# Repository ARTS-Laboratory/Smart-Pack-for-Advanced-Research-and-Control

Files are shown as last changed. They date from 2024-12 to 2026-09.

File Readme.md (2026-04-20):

# Smart-Pack-for-Advanced-Research-and-Control (SPARC)
The SPARC Pack is an open-source, research-grade battery system designed to advance thermal and electro-thermal modeling techniques while integrating state-of-the-art sensing and Battery Management System (BMS) technologies. Its modular design supports both cylindrical and pouch cell configurations, enabling cutting-edge investigations into battery performance, health, and reliability under diverse operating conditions.

## Variations

### Camden
A pack designed around the Samsung 30Q as a 10S1P nominal 40 V pack. 

## Licensing and Citation

This work is licensed under a Creative Commons Attribution-ShareAlike 4.0 International License [cc-by-sa 4.0].



Cite this as: 

@Misc{ARTSLabSmartPackAdvanced,    
  author = {ARTS-Lab},  
  howpublished = {GitHub},  
  title  = {Smart-Pack-for-Advanced-Research-and-Control},    
  groups = {ARTS-Lab},    
  url    = {https://github.com/ARTS-Laboratory/Smart-Pack-for-Advanced-Research-and-Control},   
  note  = {Accessed: Month dd, yyyy},   
}

<p align="center">
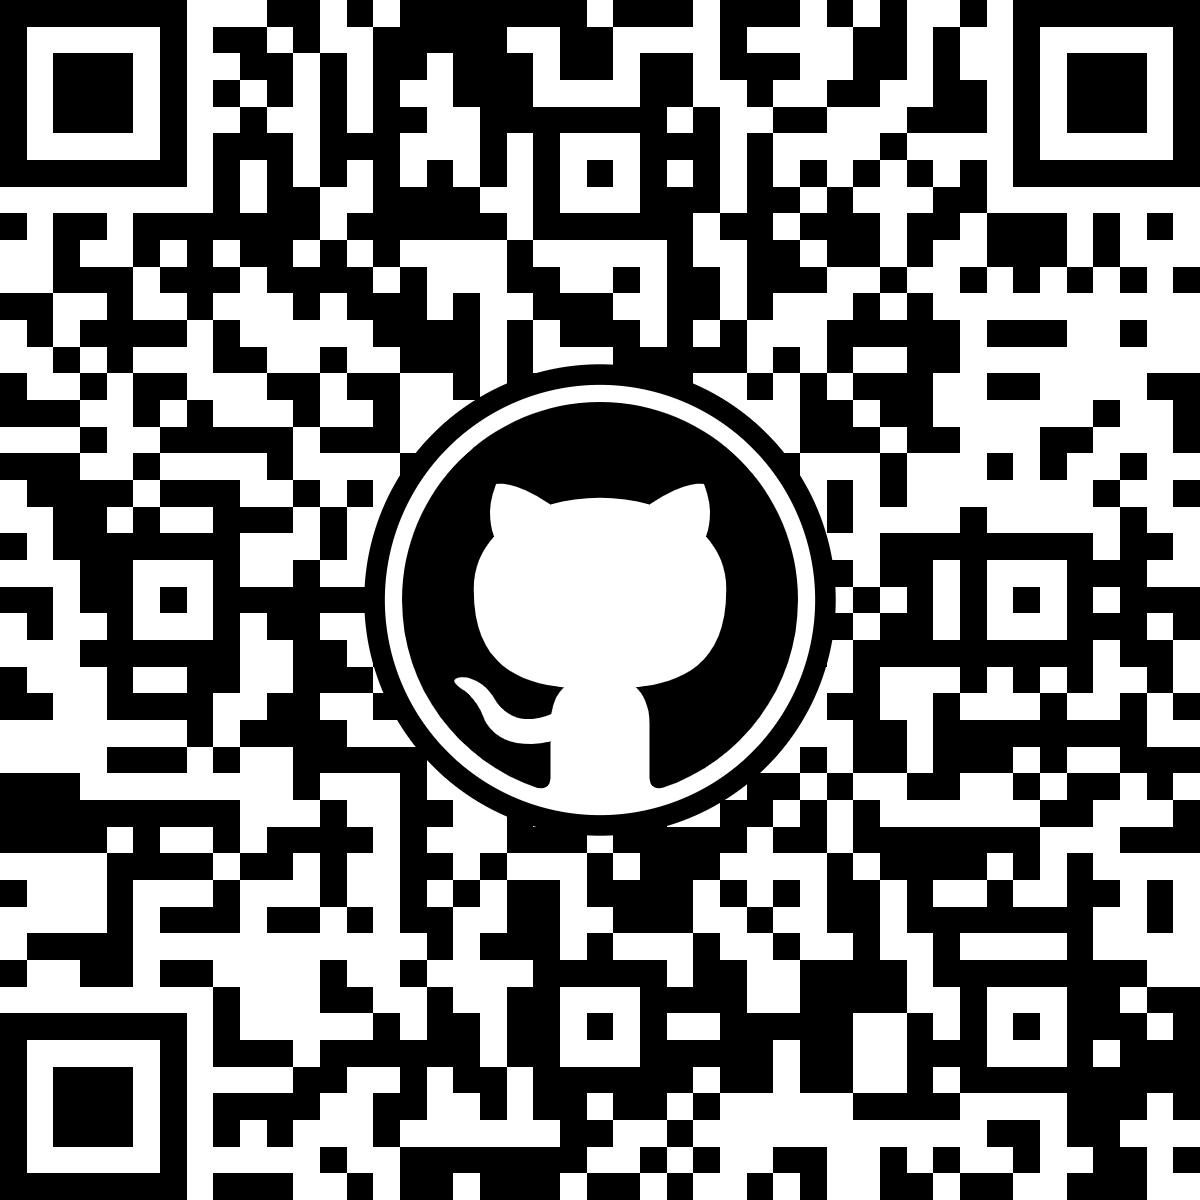
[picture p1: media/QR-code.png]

</p>
<p align="center">
QR code for repo.
</p>

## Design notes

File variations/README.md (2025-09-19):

# Variations
Variations of the battery packs are named after cities in South Carolina with Amtrack Stations.

## Camden
A pack designed around the Samsung 30Q as a 10S1P nominal 42 V 30 Ah pack. 

## Columbia
A pack designed around the Samsung 40T as a 10S1P nominal 42 V 40 Ah pack. 

## Florence
A pack designed around the Hakadi 18650E-1500 as a 10S1P nominal 30 V 15 Ah pack. 

## Denmark
A pack designed around the LithiumWerks APR18650m1B as a 10S1P nominal 33 V 11.5 Ahr pack.

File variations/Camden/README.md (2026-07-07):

# Camden
A pack designed around the Samsung 30Q as a 10S1P nominal 42 V 30 Ah pack. 

## V0.1.0 
1. Inital desings for 10S1P
1. Uses a 3-4-3 layout

## V0.2.0
1. stable 3D print setups

## V0.2.1
1. Sense wires on the packs.
1. Snap fits.
1. Single design for top and bottom.

## V0.2.2
1. More defined DIN-rail system
2. Different plastic frames form top and bottom
3. PCBs for BMS

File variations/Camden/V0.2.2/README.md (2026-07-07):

# Camden V0.2.2
This version puts the pack onto a back board with a DIN Rail

This project uses KiCAD 9.0.5 https://downloads.kicad.org/kicad/windows/explore/stable/download/kicad-9.0.5-x86_64.exe and Inventor 2025 Q2

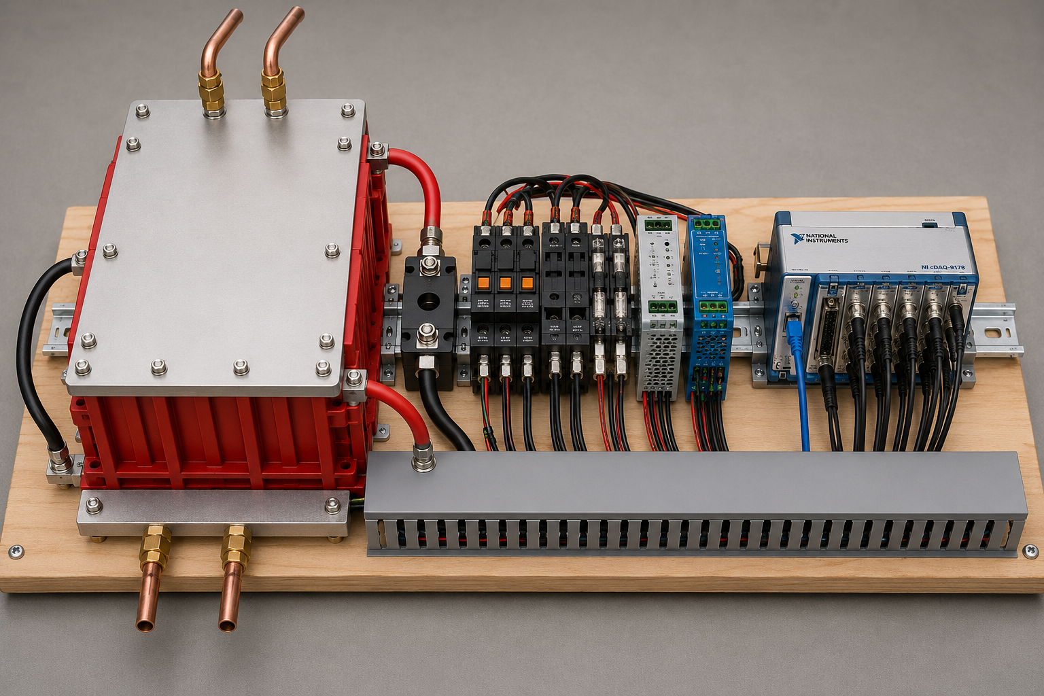
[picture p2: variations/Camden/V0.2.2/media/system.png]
 <br> 
<p style="text-align: center;"> Desing vison image of the proposed SPARC system.</p>

</p>

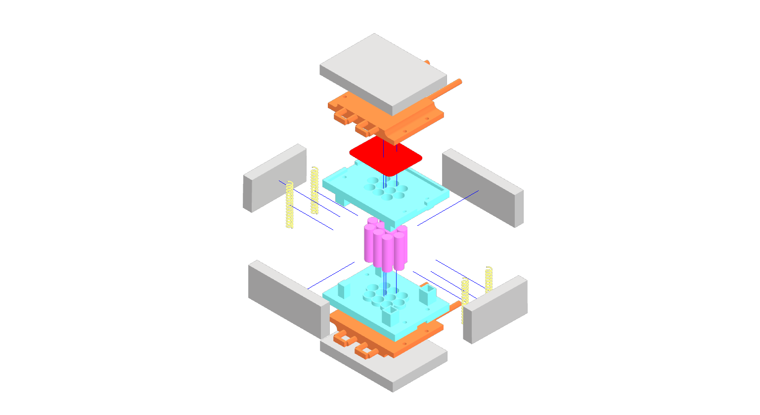
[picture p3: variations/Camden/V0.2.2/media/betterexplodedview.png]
 <br> 
<p style="text-align: center;"> The battery pack design.</p>

</p>

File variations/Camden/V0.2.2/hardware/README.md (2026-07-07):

# Hardware

## Todo notes (mark when done)
1. Make a top and bottom
1. Delete all the CAD files that are nto 18550 and you don't need. 
1. Extend the gap between the slot down and the first and last cell. Move the edge out more if needed. 
1. Rotate bolt hole 90* so the flat end faces out. 
1. Label them cells 0-9 
1. Replace ARTS-LAB with "Frame top" or whatever the name of the inventor file is. 
1. Add ARTS-LAB but bigger and on the side as just Branding. 
1. Think on the connectors, the will be updates, but maybe not now.

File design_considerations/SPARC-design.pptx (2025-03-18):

## Smart-Pack-for-Advanced-Research-and-Control (SPARC)

## Why Develop a Modular, Sensor-Rich Battery System?

- Supports Next-Generation Energy Storage
  - Enables research on distributed energy systems and high-performance battery management
  - Facilitates scalability for a wide range of power applications
- Enhances Digital Twin Development
  - Real-time, high-fidelity data streams enable dynamic model validation and predictive analytics
  - Integrated sensors allow continuous updates to electrochemical, thermal, and mechanical models
- Enables Flexible and Configurable Testing
  - Modular 42V (10S1P) design allows for series/parallel stacking to replicate different battery pack architectures
  - Supports multiple cell sizes and chemistries (e.g., 18650, 21700, NMC, LFP) for diverse application studiesImproves
- Advanced Battery Control and Monitoring
  - High-resolution BMS with CompactDAQ integration enables real-time state estimation and anomaly detection
  - Adaptive energy management through advanced control strategies

## Why Not Just Buy a Battery Pack?

- It’s Not That Simple
  - Off-the-shelf battery packs are designed for consumer or industrial use, not for research and experimentation
  - Most commercial packs come with proprietary BMS systems that restrict access to raw data, limiting the ability to monitor and analyze cell-level behavior
- Limited Experimental Flexibility
  - Research often requires testing individual cells and full packs under identical conditions, which isn’t possible with third-party pack builders
  - By sourcing cells from a single batch, researchers can compare degradation, thermal response, and electrochemical performance at both cell and pack levels
  - Pack design constraints in commercial solutions prevent studies on alternative cooling strategies, advanced sensing, and new control architectures
- Need for Custom Sensing and Instrumentation
  - Commercial battery packs do not support high-resolution instrumentation, such as differential voltage sensing, strain monitoring, and acoustic emissions
  - In research, advanced sensing capabilities are critical for developing and validating digital twins, studying failure mechanisms, and improving predictive modeling
  - Custom-built packs allow for direct integration with external control and data acquisition systems, ensuring researchers have full control over charging, discharging, and monitoring parameters

## What Will the Battery Module look like?


Thermal pad

Cold plate

Assembly springs

Cells

Insulation

Cell holder

## What Will the BMS Look Like?

BMS Control Board

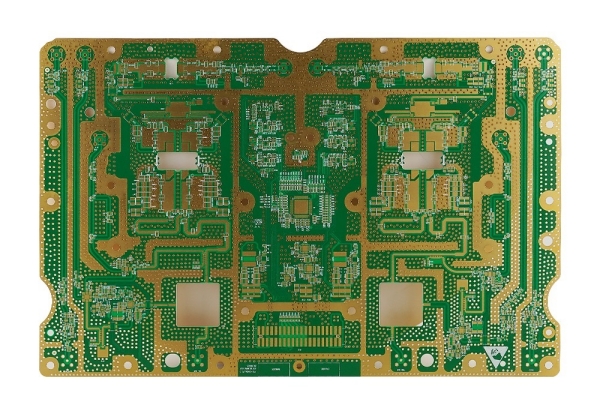
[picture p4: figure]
Custom PCB-The Ultimate Guide-ucreatepcb.com
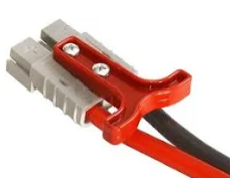
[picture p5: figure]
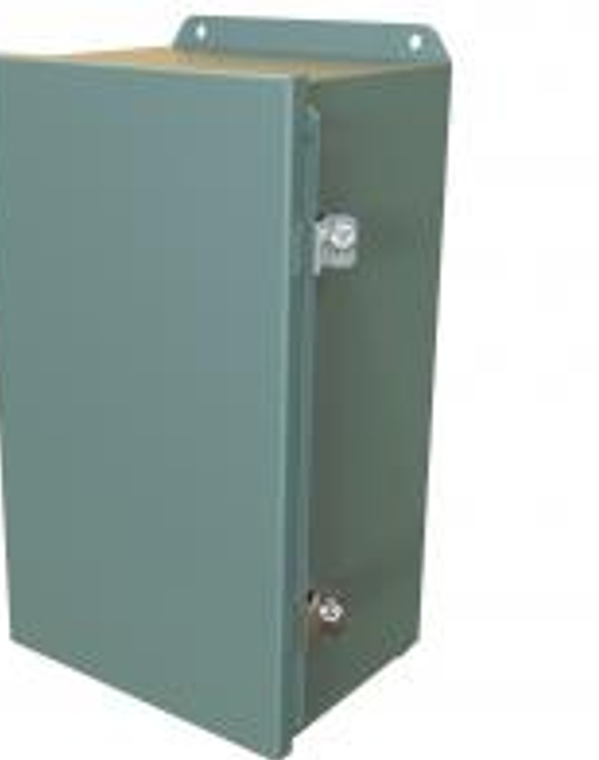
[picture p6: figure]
N4,12 J Box Hinged - 14x8x6 - Steel/Gray

Battery

Cost:
- $20,000 fully-instrumented
- $10,000 typical deployment
- $4,000 minimal viable

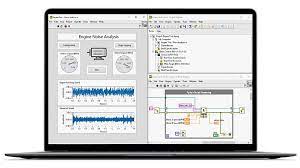
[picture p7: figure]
Zustandsüberwachung für die industrielle Fertigung - NI
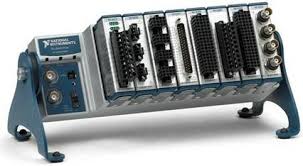
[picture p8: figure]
CompactDAQ - Wikipedia

cDAQ based DAQ

## What Features will the Pack Have

Comprehensive Sensing Capabilities
- Voltage Monitoring – Individual cell voltages and differential voltage across each cell for precise state-of-charge (SOC) estimation
- Temperature Sensors – Each cell will have dedicated temperature monitoring, ensuring thermal stability and safety
- Current Sensors – High-resolution current measurement for charge/discharge tracking and efficiency analysis
- Strain Gauges – Integrated strain sensing on cells and pack components to monitor mechanical deformation and aging effects
- Acoustic Emission Sensors – Captures high-frequency signals from crack formation, gas evolution, and early failure indicators

Advanced Battery Management Features
- Cell-Level Monitoring – Every cell is individually monitored for voltage, temperature, and strain, allowing detailed analysis of cell-to-cell variations
- Cell Balancing – Passive balancing to start, ensuring even charge distribution and extending pack lifetime
- Customizable Data Sampling – Fully open data acquisition interface, allowing researchers to modify sampling rates and data logging parameters
Open-Access and Reconfigurable Design
- Fully Open Front Panel – Allows for easy access to all monitoring points, enabling rapid sensor modifications, data acquisition customization, and external integrations
- Flexible Control Integration – Can directly support adaptive BMS algorithms and digital twin updates

## Thank You for Your Time

- Name: Austin Downey
- Title: Associate Professor
- Email: austindowney@sc.edu
- Lab GitHub: github.com/arts-laboratory

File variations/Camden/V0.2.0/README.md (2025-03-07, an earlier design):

# Camden V0.2

 <br> 
The battery pack design. 
</p>

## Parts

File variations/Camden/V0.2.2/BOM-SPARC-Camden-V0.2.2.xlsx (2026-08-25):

Designator | Component | MFR Part Number | Amount | Individual Cost | Total Cost | Notes | Vendor 1 | Vendor 2 | Vendor 3 | Vendor 4 | Vendor 5 | Vendor 6
Cells | Samsung 30Q |  | 10 | $8.22 | $82.20 |  | https://www.batteryjunction.com/products/samsung-30q-18650-3000-flat
power plug | Powerwerx PanelPlateSB1 for Anderson SB50 Series Connectors |  | 1 | $9.99 | $9.99 |  | https://powerwerx.com/anderson-sb50-panel-chassis-mount
Box | RITTAL Enclosure: Steel, 15 in x 13 in x 10 in, NEMA 4, Solid Cover, Hinged |  | 1 | $234.98 | $234.98 |  | https://www.grainger.com/product/RITTAL-Enclosure-Steel-5AAC4?opr=ILOF
Controller | cRIO-9054 |  | 1 | $3427.00 | $3427.00 |  | https://www.ni.com/en-us/shop/model/crio-9054.html | https://www.digikey.com/en/products/detail/ni/786425-01/16648375?s=N4IgTCBcDaIMYCUCSB5AtATgAwFYAsIAugL5A
strain DAQ | NI-9236 |  | 1 | $3048.00 | $3048.00 |  | https://www.ni.com/en-us/shop/model/ni-9236.html | https://www.digikey.com/en/products/detail/ni/785996-01/15219166
~~voltage module~~ | ~~NI-9221~~ |  | ~~2~~ | ~~$1106.00~~ | ~~$2212.00~~ |  | ~~https://www.ni.com/en-us/shop/model/ni-9221.html | ~~https://www.digikey.com/en/products/detail/ni/779373-01/15219106~~
Foam board | R-10 XPS Rigid Foam Board |  | 1 | $56.97 | $56.97 |  | https://www.homedepot.com/p/Owens-Corning-FOAMULAR-NGX-F-250-2-in-x-4-ft-x-8-ft-SSE-R-10-XPS-Rigid-Foam-Board-Insulation-52DDNGX/315197962
22 gauge black wire | APPROVED VENDOR Automotive Wire: TXL, 100 ft, 1 Conductor, 22 AWG, Black, 60 V Volt |  | 1 | $10.72 | $10.72 |  | https://www.grainger.com/product/Automotive-Wire-TXL-862FY9
22 gauge red wire | APPROVED VENDOR Automotive Wire: TXL, 100 ft, 1 Conductor, 22 AWG, Red, 60 V Volt |  |  | $10.72 | $10.72 |  | https://www.grainger.com/product/Automotive-Wire-TXL-862FZ5
6 gauge red and black wire | Wire-RB-06-25 |  | 1 | $90.99 | $90.99 |  | https://powerwerx.com/red-black-bonded-zip-cord
strain gauge (9 ft lead) | C4A-06-235SLA-350-39P |  | 1 | $162.72 | $162.72 |  | https://shop.micro-measurements.com/my_cart_item_list.php?v_cat_code=STRESS_ANALYSIS_STRAIN_GAGE | https://www.digikey.com/en/products/detail/micro-measurements-division-of-vishay-precision-group/MMF404146/9857834
strain gauge (3 ft lead) | C4A-06-235SLA-350-33P |  | 1 | $162.72 | $162.72 |  | https://shop.micro-measurements.com/my_cart_item_list.php?v_cat_code=STRESS_ANALYSIS_STRAIN_GAGE | https://www.digikey.com/en/products/detail/micro-measurements-division-of-vishay-precision-group/C4A-06-235SLA-350-33P/16580673
thermocouple probe | TEMPCO Thermocouple Probe: Thermocouple, Type K, 3/16 in x 3 in Probe, Grounded, Split Leads |  | 2 | $23.08 | $46.16 |  | https://www.grainger.com/product/TEMPCO-Thermocouple-Probe-Thermocouple-3AAA2?opr=ODOH&analytics=FM:Order%20History
thermocouple fitting | TEMPCO Compression Fitting: 1/8 in MNPT, For Sensor with 3/16 in OD Sheath Sensor Type |  | 2 | $7.26 | $14.52 |  | https://www.grainger.com/product/TEMPCO-Compression-Fitting-1-8-in-5ZY28?opr=ODOH&analytics=FM:Order%20History
Strain Gauge Glue (cheap option) | LOCTITE Instant Adhesive: 401, Plastics, 0.1 fl oz, Tube |  | 1 | $8.98 | $8.98 | This is the low-cost option, and we should not really use it. | https://www.grainger.com/product/LOCTITE-Instant-Adhesive-401-2VFG1?opr=ODOH&analytics=FM:Order%20History
Strain Gauge Glue | LOCTITE Instant Adhesive: 401, Plastics, 0.1 fl oz, Tube |  | 1 | $8.98 | $8.98 |  | https://www.grainger.com/product/LOCTITE-Instant-Adhesive-401-2VFG1?opr=ODOH&analytics=FM:Order%20History
cold plate | Ohmite CP4A-114A-108E-ND |  | 2 | $74.89 | $149.78 |  | https://www.digikey.com/en/products/detail/ohmite/CP4A-114A-108E/3439805
thermal pad | t-Global Technology 1168-TG-AH486-150-150-1.0-0-ND |  | 2 | $10.17 | $20.34 |  | https://www.digikey.com/en/products/detail/t-global-technology/TG-AH486-150-150-1-0-0/3042048
Barb fitting | SPEEDAIRE Barbed Hose Fitting: For 5/16 in Hose I.D., Hose Barb x NPT, 5/16 in x 1/4 in Fitting Size |  | 8 | $1.77 | $14.16 |  | https://www.grainger.com/product/SPEEDAIRE-Barbed-Hose-Fitting-For-3-6AFN8
panel mount dual female mpt | Anchor Coupling: Brass, 3/8 in x 3/8 in Fitting Pipe Size, Male NPT x Female NPT |  | 2 | $23.66 | $47.32 |  | https://www.grainger.com/product/PARKER-Anchor-Coupling-Brass-13Y869?opr=ODOH&analytics=FM:Order%20History
braded PVC tubing | Tubing: PVC, 3/8 in Inside Dia, 1/2 in Outside Dia, 5 ft Lg, Clear, Polyester Braid |  | 1 | $15.02 | $15.02 |  | https://www.grainger.com/product/Tubing-PVC-742T39?gclsrc=aw.ds&gad_source=1&gad_campaignid=21369463827
hose clamp | Fuel Injection Hose Clamp: Zinc-Plated Steel Band, 1/2 in – 9/16 in Dia., SAE # 6, 10 PK |  | 1 | $12.46 | $12.46 |  | https://www.grainger.com/product/Fuel-Injection-Hose-Clamp-5CZC5
panel Ethernet | FINECABLES Connector: Cat5e/Cat6, Industrial, Panel, Female, Phosphor Bronze, IP67, Female |  | 1 | $15.13 | $15.13 |  | https://www.grainger.com/product/808CD1?gad_source=1&gad_campaignid=21375776111&gclsrc=aw.ds
DIN rail power supply | MEAN WELL USA Inc. 1866-3518-ND |  | 1 | $29.30 | $29.30 |  | https://www.digikey.com/en/products/detail/mean-well-usa-inc/NDR-120-24/7705220
DIN Rail | APPROVED VENDOR Mounting Track: DIN Rail Mounting, Aluminum, 35 mm Wd, 305 mm Lg |  | 1 | $4.09 | $4.09 |  | https://www.grainger.com/product/Mounting-Track-DIN-Rail-Mounting-18Z759
DIN Rail 80 amp breaker | SIEMENS IEC Supplementary Protector: 80 A Amps, 72V DC, 10kA at 230/400V AC, Screw Clamp |  | 1 | $147.52 | $147.52 |  | https://www.grainger.com/product/SIEMENS-IEC-Supplementary-Protector-30XZ33
power contacts | Anderson Power Products 5900-BK |  | 4 | $1.45 | $5.80 |  | https://www.digikey.com/en/products/detail/anderson-power-products-inc/5900-BK/10650563
Ethernet cable | MONOPRICE Voice and Data Patch Cord: Unshielded, Cat 5e, 1 ft |  | 1 | $1.46 | $1.46 |  | https://www.grainger.com/product/5PZR3?gclsrc=aw.ds&gad_source=1&gad_campaignid=21379885351
thermocouple input module | NI-9213 |  | 1 | $2195.00 | $2195.00 |  | https://www.ni.com/en-us/shop/model/ni-9213.html | https://www.digikey.com/en/products/detail/ni/785185-01/15218920
TEMPCO Thermocouple Wire | TEMPCO Thermocouple Wire: Type J, 20 AWG Conductor Size, 100 ft |  | 1 | $99.89 | $99.89 |  | https://www.grainger.com/product/TEMPCO-Thermocouple-Wire-Type-K-3AGF3
Thermocouple, Type K | Bead Wire Temperature Probe: Thermocouple, Type K, Ungrounded, Mini Plug, Bolt-On |  | 10 | $6.92 | $69.20 |  | https://www.grainger.com/product/Bead-Wire-Temperature-Probe-4JPL6
D-sub 25 break out | Phoenix Contact 2761619 |  | 2 | $72.75 | $145.50 |  | https://www.digikey.com/en/products/detail/phoenix-contact/2761619/349453
voltage sense wire | 22 gauge solid hook up wire |  | 5 | $3.44 | $17.20 |  | https://www.digikey.com/en/products/detail/sparkfun-electronics/08023/6833929
6 gauge ring connectors | Molex 0191930226 |  | 2 | $1.15 | $2.30 |  | https://www.digikey.com/en/products/detail/molex/0191930226/1952713
Nickel Strips | Nickel Strips For Lithium Battery Pack Welding (10m 0.2X6mm) |  | 1 | $14.65 | $14.65 |  | https://www.aliexpress.us/item/3256805148780496.html?gatewayAdapt=glo2usa4itemAdapt
3/8 in Tee | Tee: Red Brass, 3/8 in x 3/8 in x 3/8 in Fitting Pipe Size, Female NPT x Female NPT x Female NPT |  | 2 | 9.85 | $19.70 |  | https://www.grainger.com/product/Tee-Red-Brass-1VEZ1?opr=PDPRRDSP&analytics=dsrrItems_1CPF5
PLA | PLA Basic - red |  | 1 | $19.99 | $19.99 |  | https://us.store.bambulab.com/products/pla-basic-filament?id=40475107000456
115V power plug | IEC C14 SCREW ON PANEL MOUNT W |  | 1 | $1.87 | $1.87 |  | https://www.digikey.com/en/products/detail/io-audio-technologies/IO-C14SP-63/21379594?gad_source=1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
Strain Gauge Coating | CONFORMAL COATING UL 94V-0 |  | 1 | $22.56 | $22.56 |  | https://www.digikey.com/en/products/detail/mg-chemicals/419D-55ML/9657990
tee to thermocouple reducer | Hex Bushing: Brass, 3/8 in x 1/8 in Fitting Pipe Size, Male NPT x Female NPT, Class 150 |  | 2 | 2.1 | $4.20 |  | https://www.grainger.com/product/Hex-Bushing-Brass-6AYW6
pipe through washerers | Flat Washer: 18-8, Stainless Steel, 1 in Screw Sz, 1.063 in In Dia, 2 in Out Dia, 18-8, 5 PK |  | 4 | $3.75 | $15.00 |  | https://www.grainger.com/product/Flat-Washer-18-8-22UG44
Pump | Kamoer DIP1500 Peristaltic Pump 24V 1500Ml/Min High Flow Intelligent |  | 1 | 299.54 | $299.54 |  | https://www.ebay.com/itm/405898925209?_skw=Kamoer+DIP+1500+Peristaltic+Pumps&itmmeta=01K6KVSWHYJSNG6EA2PQ3BRXEZ
stright 3/8 compression fitting | APPROVED VENDOR Compression Fitting Adapter: 3/8 in OD x 3/8 in Pipe Fitting Size, Brass |  | 2 | 6.74 | $13.48 | If you have 1 of these, you could get rid of one of the 3/8 barb fittings from the tee to the pipe | https://www.grainger.com/product/Compression-Fitting-Adapter-46M551
1 inch Hole Saw | MILWAUKEE Hole Saw: 1 in Saw Dia., 3.5 Teeth per Inch, 1 5/8 in Max. Cutting Dp, Bi-Metal |  | 1 | 15.89 | $15.89 |  | https://www.grainger.com/product/MILWAUKEE-Hole-Saw-1-in-Saw-Dia-856EV8 (https://nam02.safelinks.protection.outlook.com/?reserved=0)
Extension Spring | Music-Wire Steel Extension Springs with Hook Ends |  | 4 | $2.07 | $8.28 | the total cost is actually the price of 6 since that is the lowest it is sold at | https://www.mcmaster.com/9432K48/ | https://www.fastenal.com/product/details/923785687
contact bolt | Hex Head Cap Screw: Stainless Steel, A2, Plain, M6-1.00, Coarse, 16 mm lg, |  | 1 | $4.36 | $4.36 | pack of 50, need 2 | https://www.grainger.com/product/Hex-Head-Cap-Screw-Stainless-22TF95
contact nut | Hex Nut: Std Hex, M6x1.00 Thread, 10 mm Hex Wd, 5 mm Hex Ht, Stainless Steel, 18-8, Plain, 50 PK |  | 1 | $2.73 | $2.73 | pack of 50, need 2 | https://www.grainger.com/product/Hex-Nut-Std-Hex-22YK33
contact washer | Flat Washer: 18-8, Stainless Steel, M6 Screw Sz, 6.62 mm In Dia, 12 mm Out Dia, 18-8, 50 PK |  | 1 | $1.20 | $1.20 | pack of 50, need 2 | https://www.grainger.com/product/Flat-Washer-18-8-26WC34
NI Analog Voltage in | NI-9209 with D-sub (783729-01) |  | 1 | $1414.12 | $1414.12 |  | https://www.ni.com/en/shop/hardware/voltage/model-ni-9209 | https://www.digikey.com/en/products/detail/ni/783729-01/15219085 | https://www.newark.com/ni/783729-01/ni-9209-voltage-input-module-24bit/dp/13AJ4083
Dsub connector | Amphenol ICC (FCI) D37S13A6GX00LF |  | 1 | $7.37 | $7.37 |  | https://www.digikey.com/en/products/detail/amphenol-cs-fci/D37S13A6GX00LF/1538196
Dsub cable | CABLE DB37M/F DBL SHLD 1' |  | 1 | $108.06 | $108.06 |  | https://www.digikey.com/en/products/detail/l-com/CS2N37MF-1/21287760
wire duct | Thomas & Betts Wiring Duct, 2 × 2 in, 72 in, PVC, Gray | TYD2X2WPG6 | 1 | $34.10 | $34.10 | Wide-slot, screw-mount | https://www.grainger.com/product/THOMAS-BETTS-Wiring-Duct-2-in-Nom-Wd-53UH84
wire duct cover | Thomas & Betts Wiring Duct Cover, 2 in, 72 in, PVC, Gray | TYD2CPG6 | 1 | $13.76 | $13.76 | Snap-on cover for 2 in wiring duct | https://www.grainger.com/product/THOMAS-BETTS-Wiring-Duct-Cover-PVC-53UH87
 |  |  |  | Total | $14517.78

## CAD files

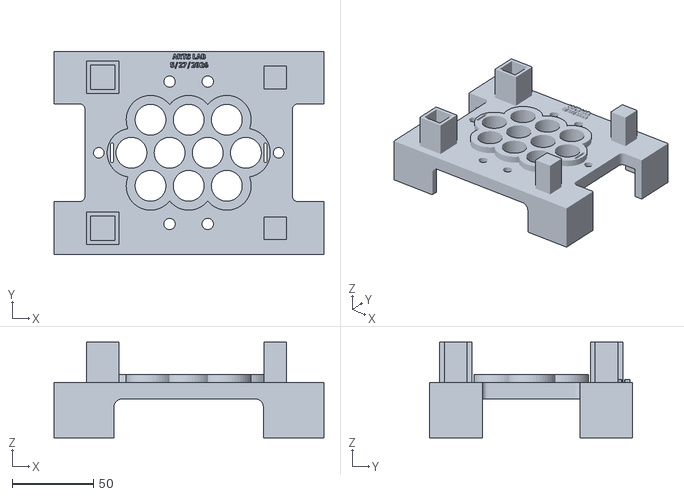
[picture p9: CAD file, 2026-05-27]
variations/Camden/V0.2.2/hardware/18650_Pack_CAD/Pillars_Cellcase_18650.stl
166.3 x 125.1 x 59.0

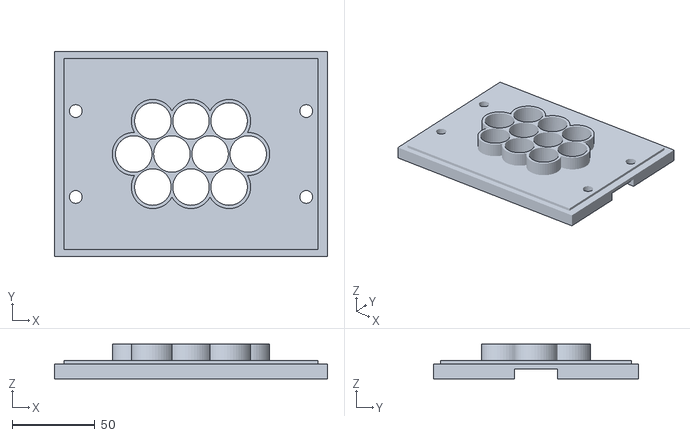
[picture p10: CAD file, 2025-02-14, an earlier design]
variations/Camden/V0.1.0/CELLCASE21700.stl
164.6 x 123.7 x 21.0

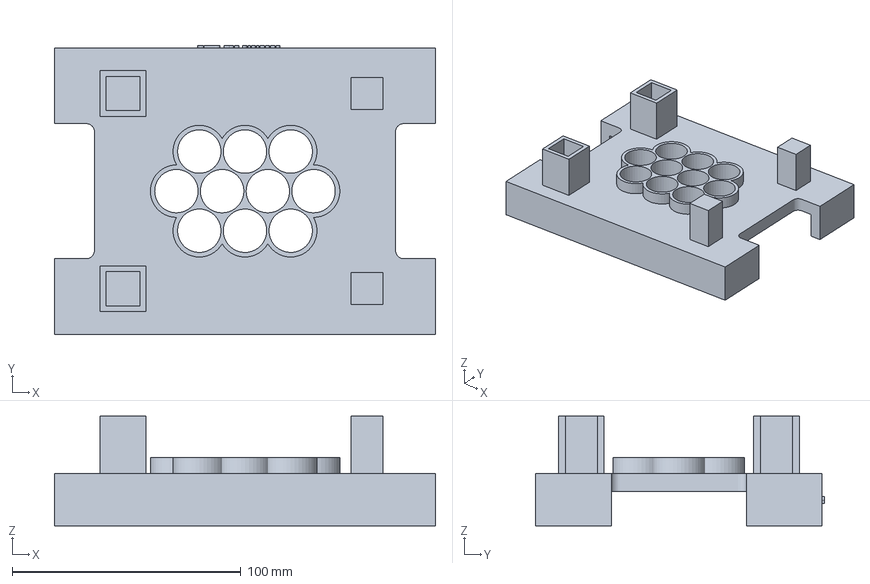
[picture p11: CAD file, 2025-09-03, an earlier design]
variations/Camden/V0.2.0/PILLARSCELLCASE18650.3mf
166.7 x 126.4 x 48.0 mm

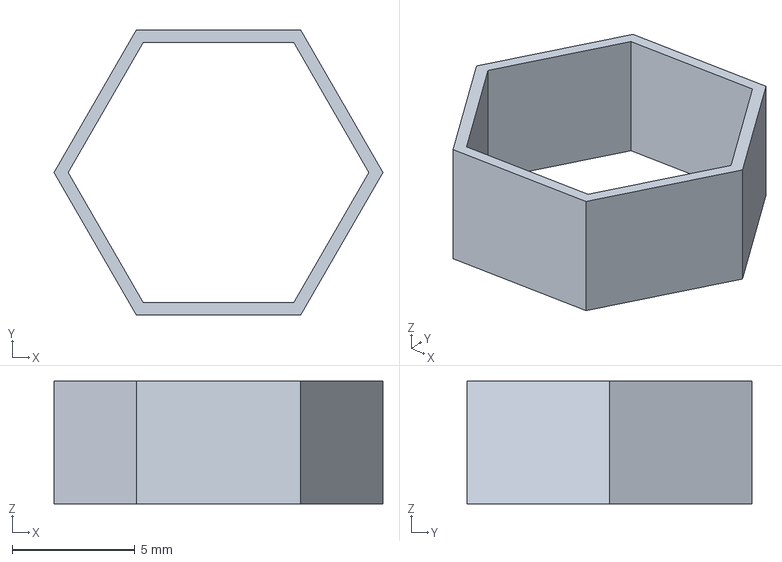
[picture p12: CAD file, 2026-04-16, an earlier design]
variations/Camden/V0.2.1/hardware/18650_Pack_Cad/tolerance_test.3mf
13.4 x 11.6 x 5.00 mm

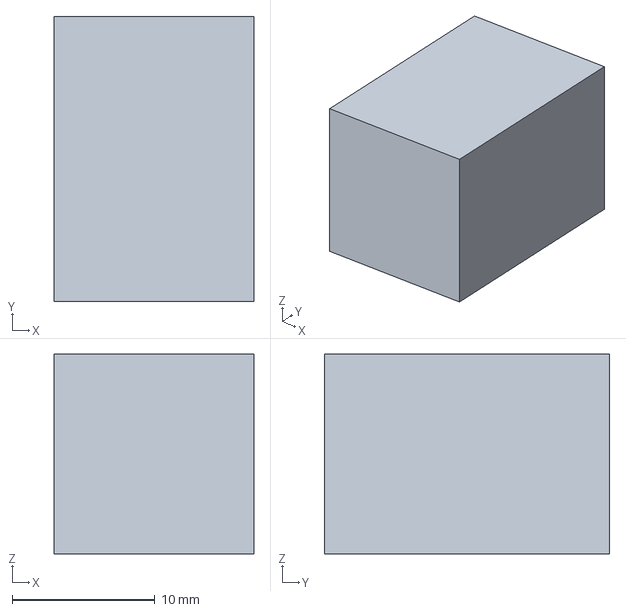
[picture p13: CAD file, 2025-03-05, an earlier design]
variations/Camden/V0.2.1/hardware/Old_Versions/PILLARStest.3mf
14.0 x 20.0 x 14.0 mm

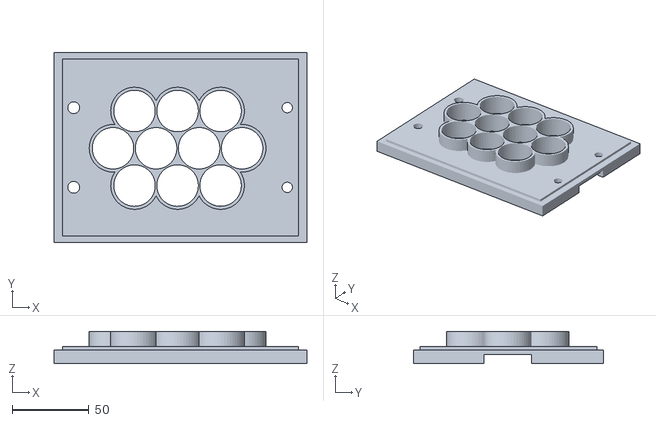
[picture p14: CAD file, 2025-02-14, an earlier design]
variations/Camden/V0.1.0/CELLCASE26650.stl
164.6 x 123.7 x 21.0

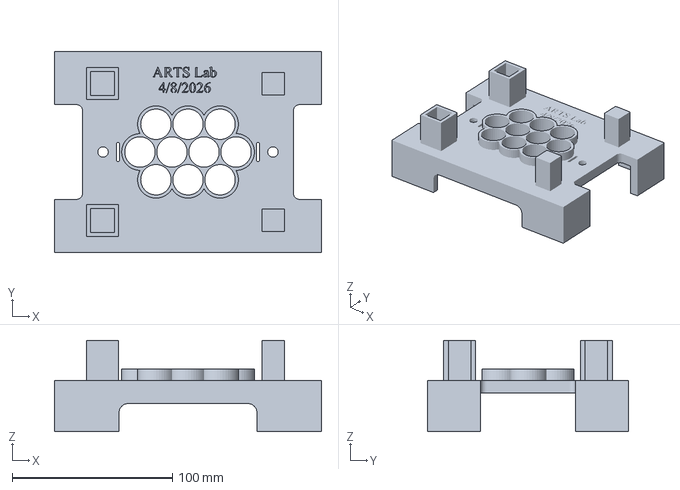
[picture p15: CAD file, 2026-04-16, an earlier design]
variations/Camden/V0.2.1/hardware/18650_Pack_Cad/Pillars_Cellcase_18650.3mf
166.7 x 125.4 x 57.0 mm

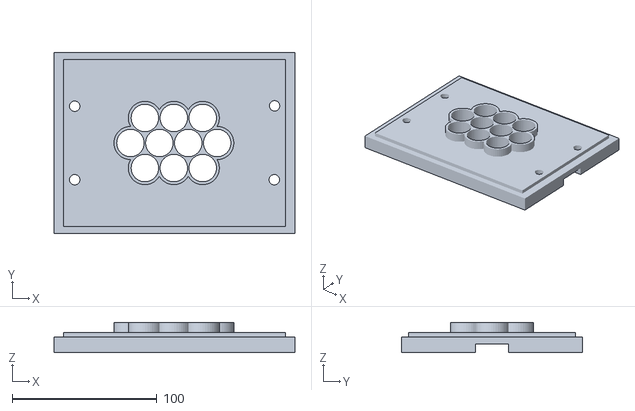
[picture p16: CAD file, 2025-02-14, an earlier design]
variations/Camden/V0.1.0/CELLCASE18650FIXED.stl
166.7 x 125.4 x 21.0

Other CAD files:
variations/Camden/V0.2.0/PILLARSCELLCASE18650.gcode.3mf
variations/Camden/V0.2.0/18650ASSEMBLYfordrawing-1.dwg
variations/Camden/V0.1.0/21700PACK.iam
variations/Camden/V0.1.0/26650(Green)_MIR.ipt
variations/Camden/V0.1.0/26650(Green)_MIR1.ipt
variations/Camden/V0.1.0/26650(Green)_MIR1_MIR.ipt
variations/Camden/V0.1.0/26650(Green)_MIR2.ipt
variations/Camden/V0.1.0/26650(Green)_MIR3.ipt
variations/Camden/V0.1.0/26650(Green)_MIR3_MIR.ipt
variations/Camden/V0.1.0/26650(Green)_MIR3_MIR1.ipt
variations/Camden/V0.1.0/26650(Green)_MIR3_MIR_MIR.ipt
variations/Camden/V0.1.0/26650(Green)_MIR4.ipt
variations/Camden/V0.1.0/26650(Green)_MIR4_MIR.ipt
variations/Camden/V0.1.0/26650(Green)_MIR5.ipt
variations/Camden/V0.1.0/26650(Green)_MIR_MIR.ipt
variations/Camden/V0.1.0/26650(Green)_MIR_MIR1.ipt
variations/Camden/V0.1.0/26650(Green)_MIR_MIR_MIR.ipt
variations/Camden/V0.1.0/343BATTERYPACK18650.iam
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

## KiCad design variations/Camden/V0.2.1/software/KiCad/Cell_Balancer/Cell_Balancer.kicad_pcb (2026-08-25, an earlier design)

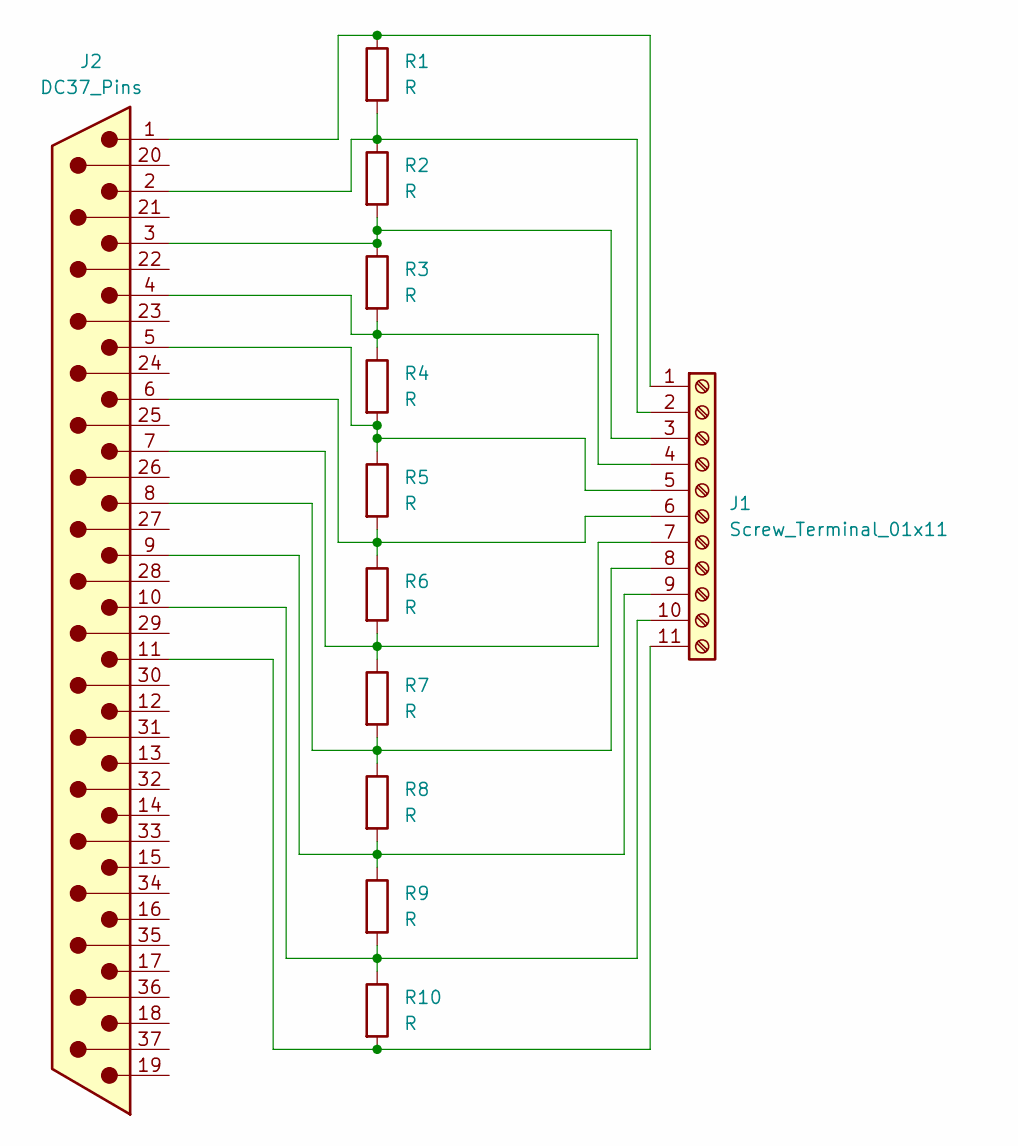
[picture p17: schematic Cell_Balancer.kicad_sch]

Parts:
J1: Screw_Terminal_01x11; TerminalBlock_Phoenix_MKDS-1,5-11_1x11_P5.00mm_Horizontal
J2: DC37_Pins; DSUB-37_Pins_Horizontal_P2.77x2.84mm_EdgePinOffset9.90mm_Ho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
R1, R2, R3, R4, R5, R6, R7, R8, R9, R10: R; R_1812_4532Metric

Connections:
unnamed: J1.1, J2.1, R1.1
unnamed: J1.2, J2.2, R1.2, R2.1
unnamed: J1.3, J2.3, R2.2, R3.1
unnamed: J1.4, J2.4, R3.2, R4.1
unnamed: J1.5, J2.5, R4.2, R5.1
unnamed: J1.6, J2.6, R5.2, R6.1
unnamed: J1.7, J2.7, R6.2, R7.1
unnamed: J1.8, J2.8, R7.2, R8.1
unnamed: J1.9, J2.9, R8.2, R9.1
unnamed: J1.10, J2.10, R9.2, R10.1
unnamed: J1.11, J2.11, R10.2

Board: 2 copper layers, 12 parts (0 on the bottom side), 11 nets, no tracks yet.

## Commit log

2025-02-14 Cad and slicer files
    These are the CAD and slicer files for the 3 variations of the battery pack. the .ipt files were made in inventor and the .stl are made with the bambu slicer
    [BatteryCasev1.ipt, CELLCASE18650FIXED.stl, CELLCASE21700.ipt, CELLCASE21700.stl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]
2025-02-26 Cad and Slicer Files
    [BatteryCasev1.ipt, CELLCASE18650FIXED.stl, CELLCASE21700.ipt, CELLCASE21700.stl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]
2025-02-28 CAD file
    Variation 2 involves having a male and female pillar in order to help facilitate good thermal contact
    [PILLARSCELLCASE18650.ipt]
2025-03-03 IPT files
    [PILLARSCELLCASE18650.0002.ipt, PILLARSCELLCASE18650.ipt]
2025-03-03 CAD files
    [PILLARSCELLCASE18650.3mf, PILLARSCELLCASE18650.stl]
2025-03-04 ipt files
    The pillars now make contact on the make and female sections, instead of just being slots
    [PILLARSCELLCASE18650.0002.ipt, PILLARSCELLCASE18650.0004.ipt, PILLARSCELLCASE18650.ipt, PILLARSCELLCASE18650.stl]
2025-03-04 ipt file
    This 3d model is a tool to make sure the tolerance on the main part is good
    [PILLARStest.0001.ipt, PILLARStest.ipt, PILLARStest.stl]
2025-03-04 Slicer files
    [PILLARSCELLCASE18650.3mf, PILLARSCELLCASE18650.gcode.3mf]
2025-06-10 Added pillars case for the 21700 cell
    [CELLCASE21700.ipt, PILLARSCELLCASE18650 - Copy.0013.ipt, PILLARSCELLCASE18650.0012.ipt, PILLARSCELLCASE18650.0013.ipt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]
2025-08-08 Added project box CAD
    [sc121212nk.0001.iam, sc121212nk.iam, sc121212nk_01.ipt, sc121212nk_02.ipt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]
2025-08-10 2nd CAD model added
    [F161410HC1.ipt, JB161410HC (1).iam, JBMP1614.ipt, JB_HINGE.ipt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]
2025-08-10 labeled CAD Models
    [sc121212nk.iam, sc121212nk_01.ipt, sc121212nk_02.ipt, sc121212nk_03.ipt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]
2025-09-18 Camden BOM
    [BOM-SPARC-Camden-v0.2.xlsx]
2025-09-18 added tee to BOM
    [BOM-SPARC-Camden-v0.2.xlsx]
2025-09-19 added v0.2.1
    [18650(PINK).ipt, 18650ASSEMBLYfordrawing-1.dwg, 18650ASSEMBLYfordrawing.0005.iam, 18650ASSEMBLYfordrawing.0005.ipn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]
2025-09-19 updated BOM
    [BOM-SPARC-Camden-V0.2.1.xlsx, BOM-SPARC-Camden-v0.3.xlsx]
2025-09-25 Clean Up
    Deleted files that are dependent on non existing files, will replace them later. organized the cad models based on their cell type. deleted redundant files
    [18650ASSEMBLYfordrawing-1.dwg, 18650ASSEMBLYfordrawing.iam, 18650ASSEMBLYfordrawing.ipn, 18650_Pink.ipt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]
2025-09-27 updated BOM with 3/8 pluming parts
    [BOM-SPARC-Camden-V0.2.1.xlsx]
2025-09-30 embossing
    Changed the embossing on the pack cad file. this will need to be updated every time the model is printed
    [Pillars_Cellcase_18650.0020.ipt, Pillars_Cellcase_18650.ipt, Pillars_Cellcase_18650.stl]
2025-10-10 new print
    [Pillars_Cellcase_18650.3mf, Pillars_Cellcase_18650.stl]
2025-10-22 Update
    made slight alteration to pack model to account for tubes poking out of cooling plate
    [Pillars_Cellcase_18650.3mf, Pillars_Cellcase_18650.gcode.3mf, Pillars_Cellcase_18650.stl]
2025-10-27 Added a part to BOM
    [BOM-SPARC-Camden-V0.2.1.xlsx]
2026-01-05 Updated BOM
    added spring
    [BOM-SPARC-Camden-V0.2.1.xlsx]
2026-01-07 adjusted the snap in place component of the cell holder
    [Pillars_Cellcase_18650.0025.ipt, Pillars_Cellcase_18650.0026.ipt, Pillars_Cellcase_18650.ipt]
2026-03-07 Made a second cooling plate. Simple rectangle made of aluminum
    [Convection_Cooling_Plate.ipt, Cooling_Plate - Copy.0013.ipt]
2026-03-07 changed design of the cellcase
    [Pillars_Cellcase_18650.0028.ipt, Pillars_Cellcase_18650.0032.ipt, Pillars_Cellcase_18650.ipt, Pillars_Cellcase_18650.stl]
2026-04-02 made improvements to cad model
    [Pillars_Cellcase_18650.0032.ipt, Pillars_Cellcase_18650.0033.ipt, Pillars_Cellcase_18650.ipt]
2026-04-02 changed dimensions of the convection plate
    [Convection_Cooling_Plate.0014.ipt, Convection_Cooling_Plate.ipt]
2026-04-08 updated dessign
    [Pillars_Cellcase_18650.0035.ipt, Pillars_Cellcase_18650.0036.ipt, Pillars_Cellcase_18650.ipt]
2026-04-15 added tolerances, and a way to check if tolerance is good
    [Pillars_Cellcase_18650.0037.ipt, Pillars_Cellcase_18650.0038.ipt, Pillars_Cellcase_18650.3mf, Pillars_Cellcase_18650.ipt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]
2026-04-17 added more materials to the BOM
    [BOM-SPARC-Camden-V0.2.1.xlsx]
2026-05-12 fixed dimensional issues in both original coooling plate and convection cooling plate
    [Convection_Cooling_Plate.0015.ipt, Convection_Cooling_Plate.0016.ipt, Convection_Cooling_Plate.ipt, Cooling_Plate.0012.ipt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]
2026-05-21 New Case
    Added a new version with the newest case. this required a new folder because it is a major redesign
    [Pillars_Cellcase_18650.0040.ipt, Pillars_Cellcase_18650.0041.ipt, Pillars_Cellcase_18650.0044.ipt, Pillars_Cellcase_18650.ipt]
2026-06-03 added materials to BOM
    [BOM-SPARC-Camden-V0.2.1.xlsx]
2026-06-03 moved us back to 0.2.1
    [18650_Pink.ipt, Convection_Cooling_Plate.0016.ipt, Convection_Cooling_Plate.ipt, Cooling_Plate - Copy.0013.ipt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]
2026-06-24 added software items
    Added a simulation of the battery pack with our cell balancer as well as a pcb schematic
2026-06-29 Update BOM-SPARC-Camden-V0.2.1.xlsx
    added new sstraingauge vendor
    [BOM-SPARC-Camden-V0.2.1.xlsx]
